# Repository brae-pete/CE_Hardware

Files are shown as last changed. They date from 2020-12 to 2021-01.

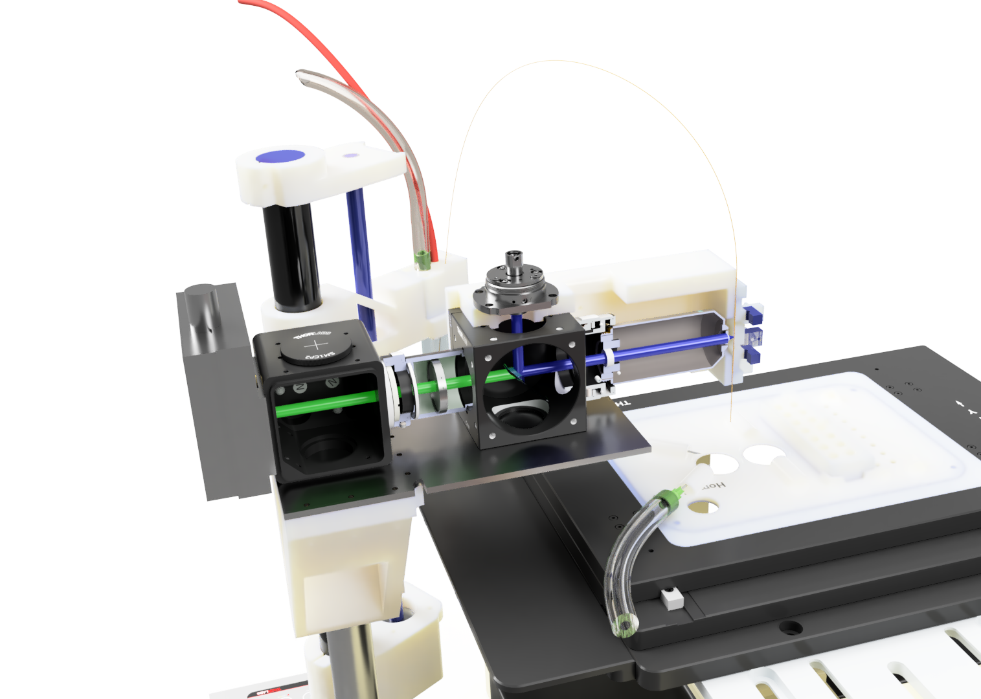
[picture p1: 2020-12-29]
Detection Assembly Light View Optical Components.png

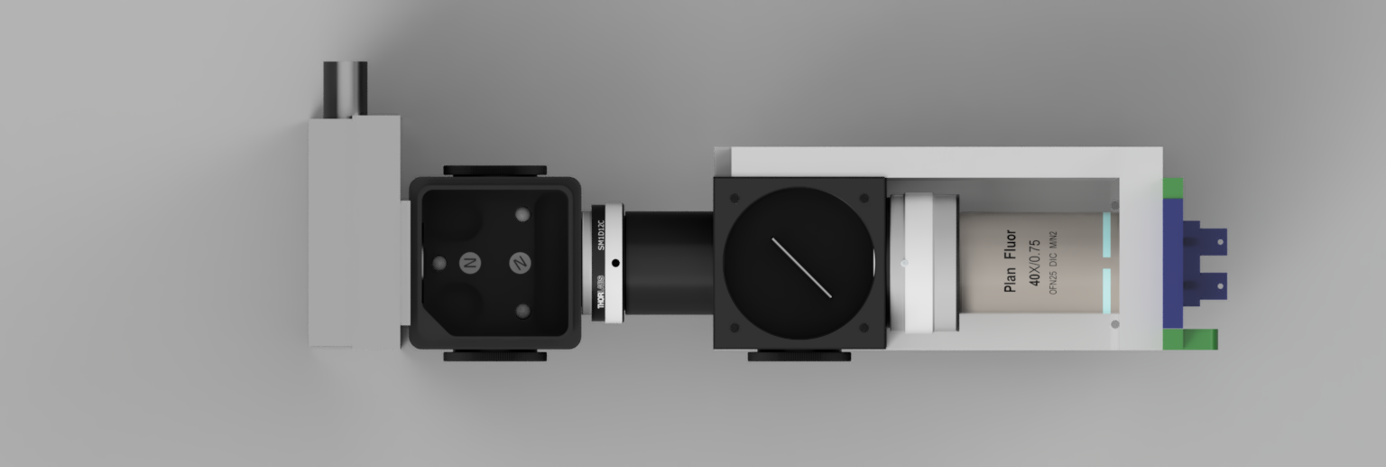
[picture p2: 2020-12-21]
CE Detection Assembly/OpticalAssemblyPurchasedComponents.png

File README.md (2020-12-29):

# CE_Hardware

Repository containing the CAD files and assemblies, as well as diagrams used to build or describe a custom CE instrumentation setup for chemical cytometry. "Assembly Notes" contains an overview of the major components for the CE instrument along with lists of materials, drawings, and diagrams for key assemblies. 

For more in depth coverage see the below articles:

**Building a Chemical cytometry system**

  Abraham, D. H., Anttila, M. M., Gallion, L. A., Petersen, B. V., Proctor, A., & Allbritton, N. L. (2019). Chapter Ten—Design of an automated capillary electrophoresis platform for single-cell analysis. In N. L. Allbritton & M. L. Kovarik (Eds.), Methods in Enzymology (Vol. 628, pp. 191–221). Academic Press. https://doi.org/10.1016/bs.mie.2019.06.016

**Description of the CE Detection assembly and performance**

  Petersen, B. V., Gallion, L., & Allbritton, N. L. (2020). Silicon Photomultipliers as a Low-Cost Fluorescence Detector for Capillary Electrophoresis. Analytical Chemistry, 92(20), 13683–13687. https://doi.org/10.1021/acs.analchem.0c03105

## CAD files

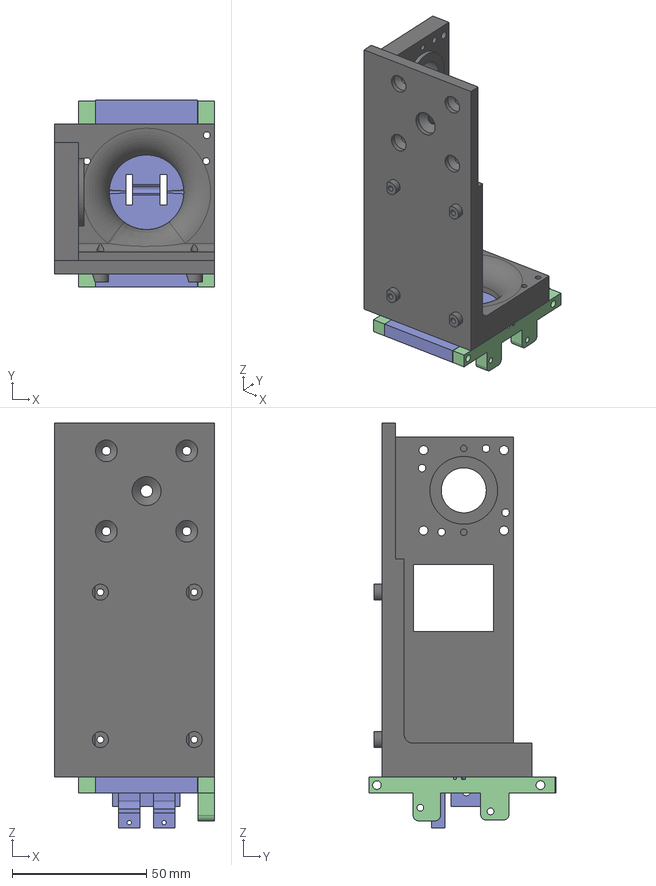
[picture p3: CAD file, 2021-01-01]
CE Detection Assembly/CapillaryAlignmentAssembly.step
59.8 x 69.8 x 151.1 mm
BarracudaCapillaryHolder_Mount v3
CapillaryArm
LowerCapillaryHolderMount
UpperCapillaryHolderMount

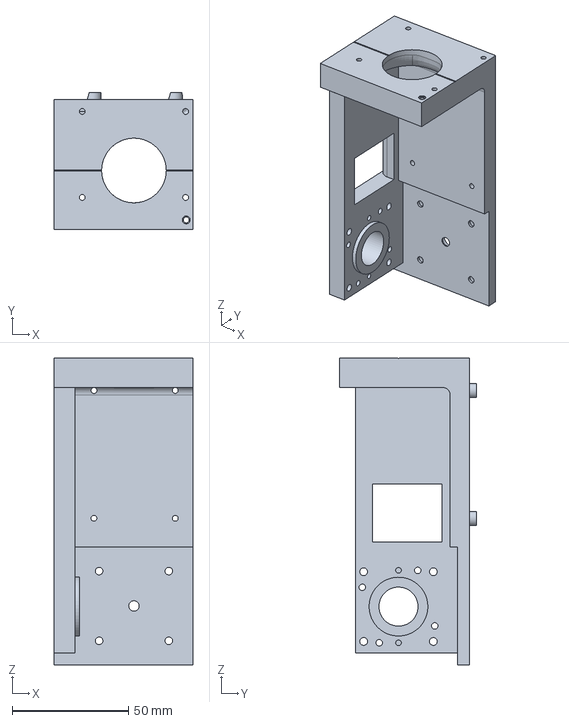
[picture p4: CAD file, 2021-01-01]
CE Detection Assembly/CapillaryArm.step
59.8 x 59.0 x 132.1 mm

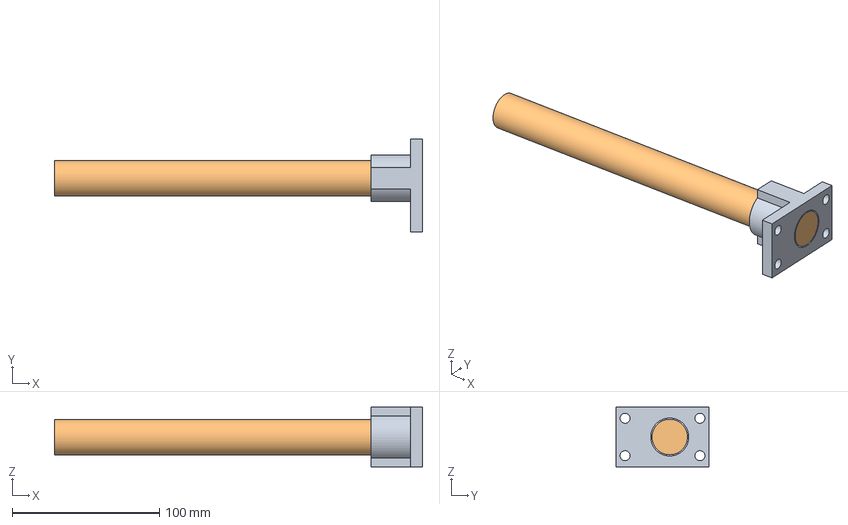
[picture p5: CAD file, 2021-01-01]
CE Detection Assembly/STL/SmoothPostMount.step
250.0 x 63.5 x 40.6 mm

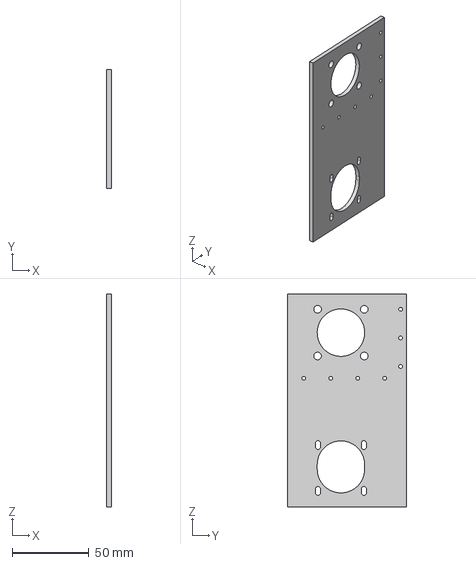
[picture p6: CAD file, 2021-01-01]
CE Detection Assembly/CantileverSupport.step
3.00 x 77.9 x 139.2 mm

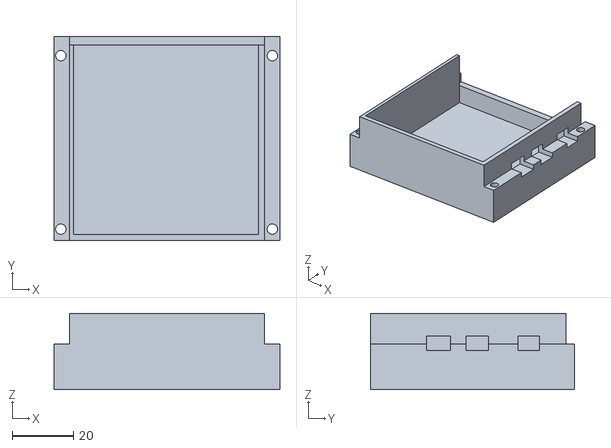
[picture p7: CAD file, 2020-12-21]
CE Detection Assembly/STL/SiPMMount_Upper+Cover.stl
74.0 x 66.8 x 25.0

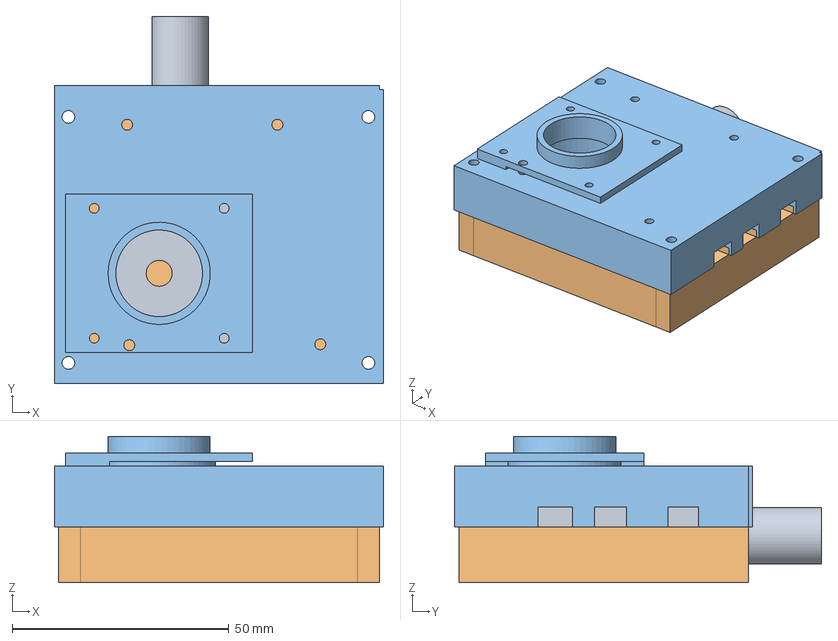
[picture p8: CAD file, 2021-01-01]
CE Detection Assembly/SiPM Mount.step
76.0 x 84.7 x 33.8 mm

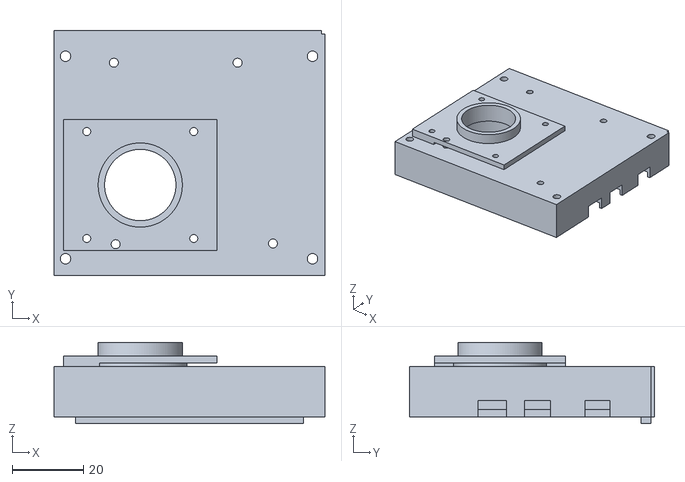
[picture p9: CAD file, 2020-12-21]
CE Detection Assembly/STL/SiPMMount_Bottom_Mount.stl
76.0 x 68.8 x 22.8

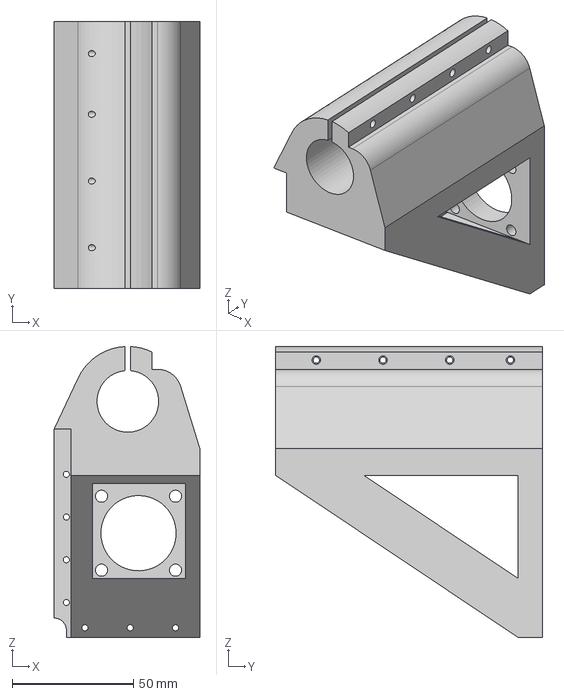
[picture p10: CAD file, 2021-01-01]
CE Detection Assembly/SmoothOpticalSupport.step
60.0 x 110.0 x 119.9 mm

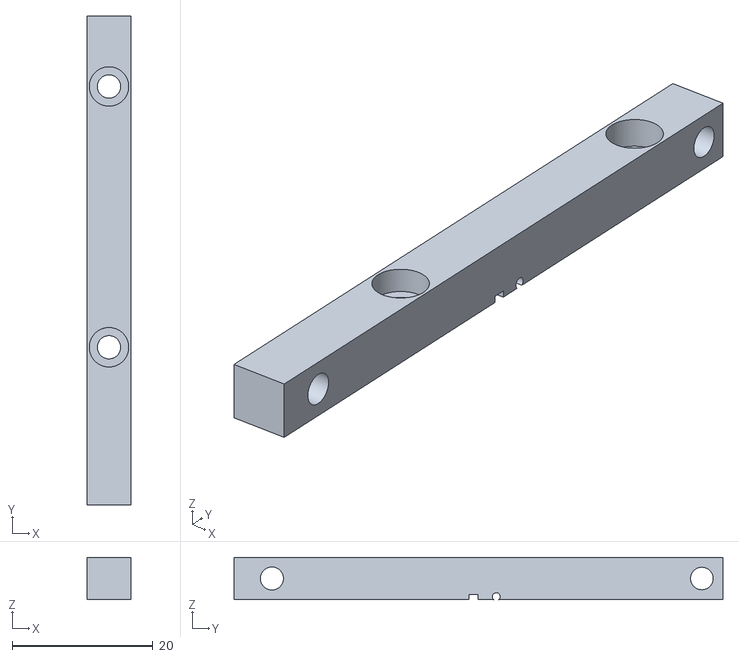
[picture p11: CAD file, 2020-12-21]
CE Detection Assembly/STL/UpperCapillaryHolderMount.stl
6.20 x 69.4 x 6.00

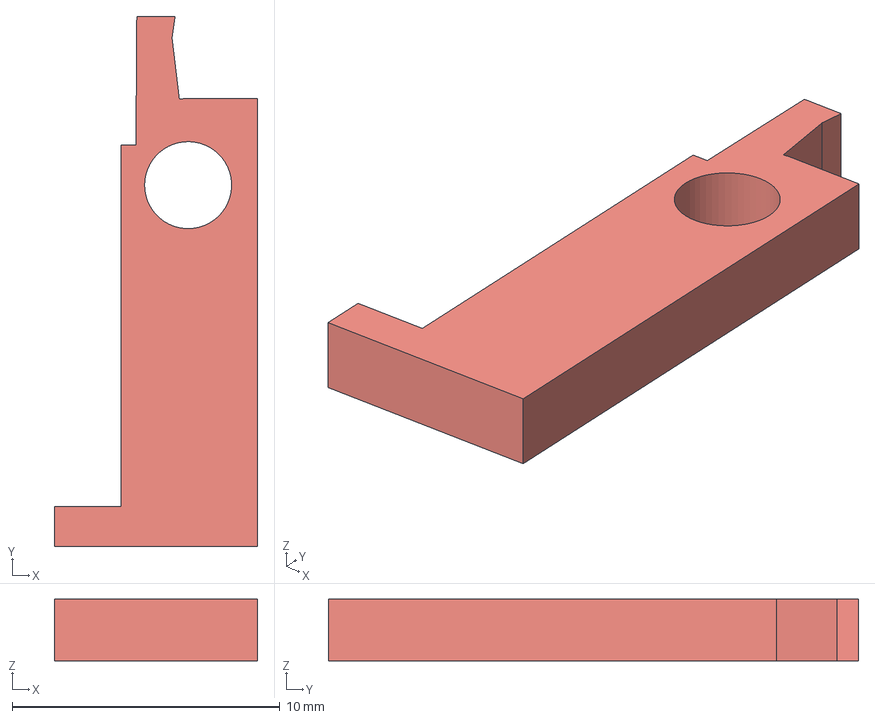
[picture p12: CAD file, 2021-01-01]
CE Detection Assembly/Lever.step
7.60 x 19.8 x 2.30 mm

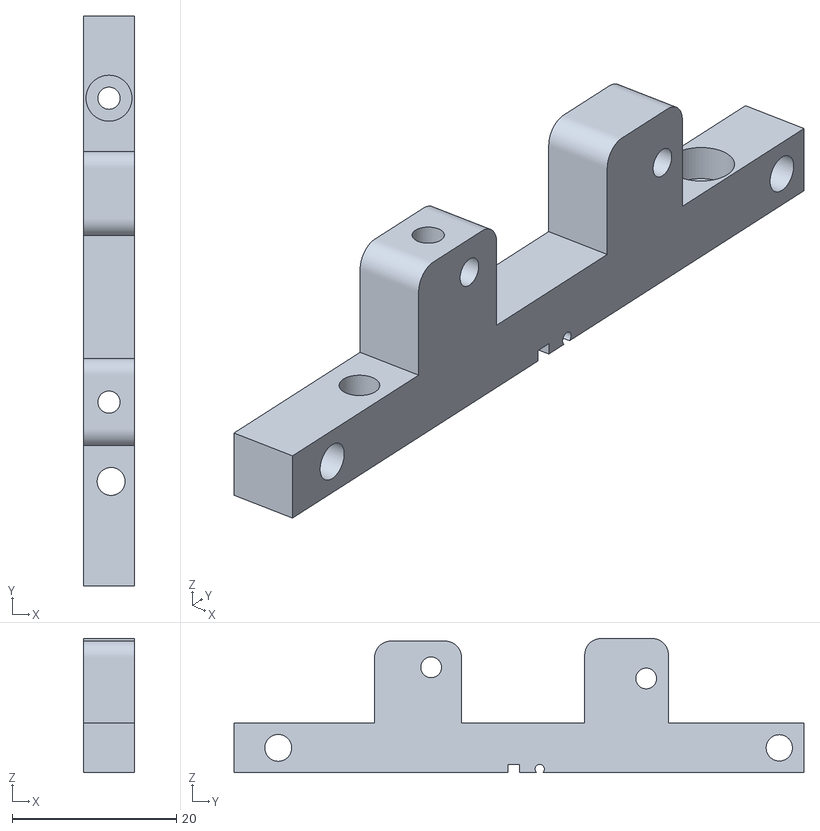
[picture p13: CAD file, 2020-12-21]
CE Detection Assembly/STL/LowerCapillaryHolderMount.stl
6.20 x 69.4 x 16.3

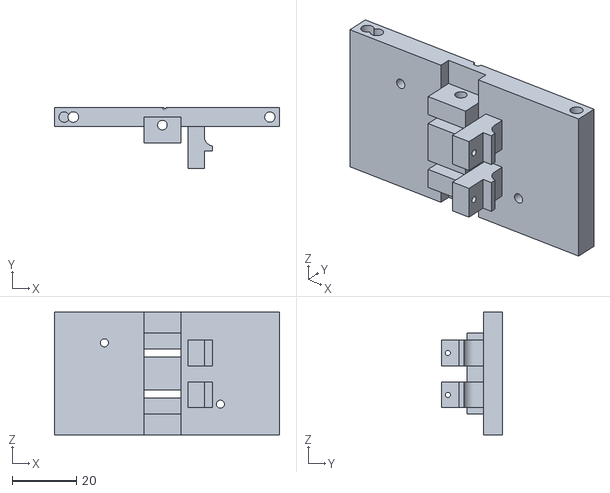
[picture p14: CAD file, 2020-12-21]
CE Detection Assembly/STL/BarracudaCapillaryHolder_Mount v3.stl
69.8 x 19.0 x 38.1

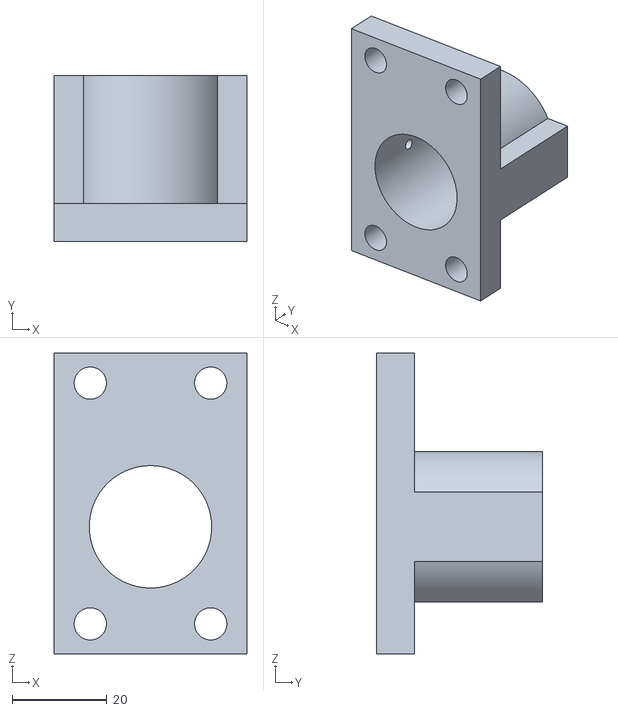
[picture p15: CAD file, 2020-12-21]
CE Detection Assembly/STL/OpticalPostMount v1.stl
40.6 x 35.0 x 63.5

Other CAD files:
CE Detection Assembly/STL/Lever v4.stl
CE Detection Assembly/STL/CantileverSupport.stl
CE Detection Assembly/STL/CapillaryArm.stl
CE Detection Assembly/SmoothPostMount.step
CE Outlet Assembly/Fusion/SmoothRod_Outlet_RemovableEnd v5.f3d

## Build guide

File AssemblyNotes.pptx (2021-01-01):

## Instrument Overview

- Hardware setup can be divided into a few key assemblies:
  - Microscope Assembly
  - CE Detection Assembly
  - CE Outlet Assembly

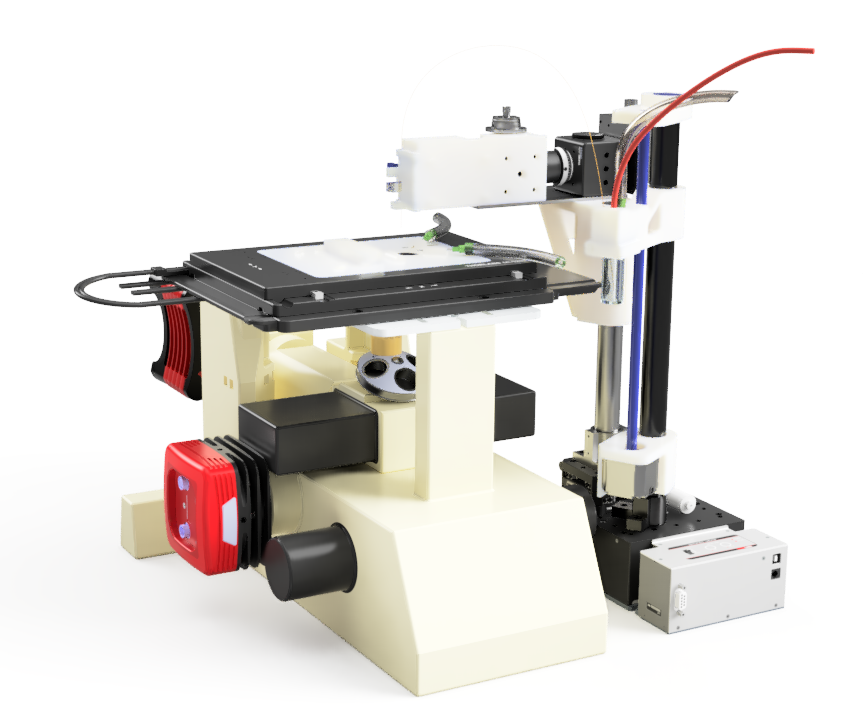
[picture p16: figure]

CE Detection Assembly

CE Outlet Assembly

Microscope Assembly

## CE Detection Assembly Custom Parts

Custom Material List

Object | Material | Fabrication
SiPM Mount | PLA/PETG | 3D Print
Capillary Arm | PLA/PETG | 3D Print
Cantilever Support | Aluminum | Mill
Optical Mount | PLA/PETG | 3D Print
Smooth Post Mount | PLA/PETG | 3D Print
Capillary Alignment Assembly | PLA/PETG | 3D Print
RGB-PCB | FR4 | EDA/PCB Fab.

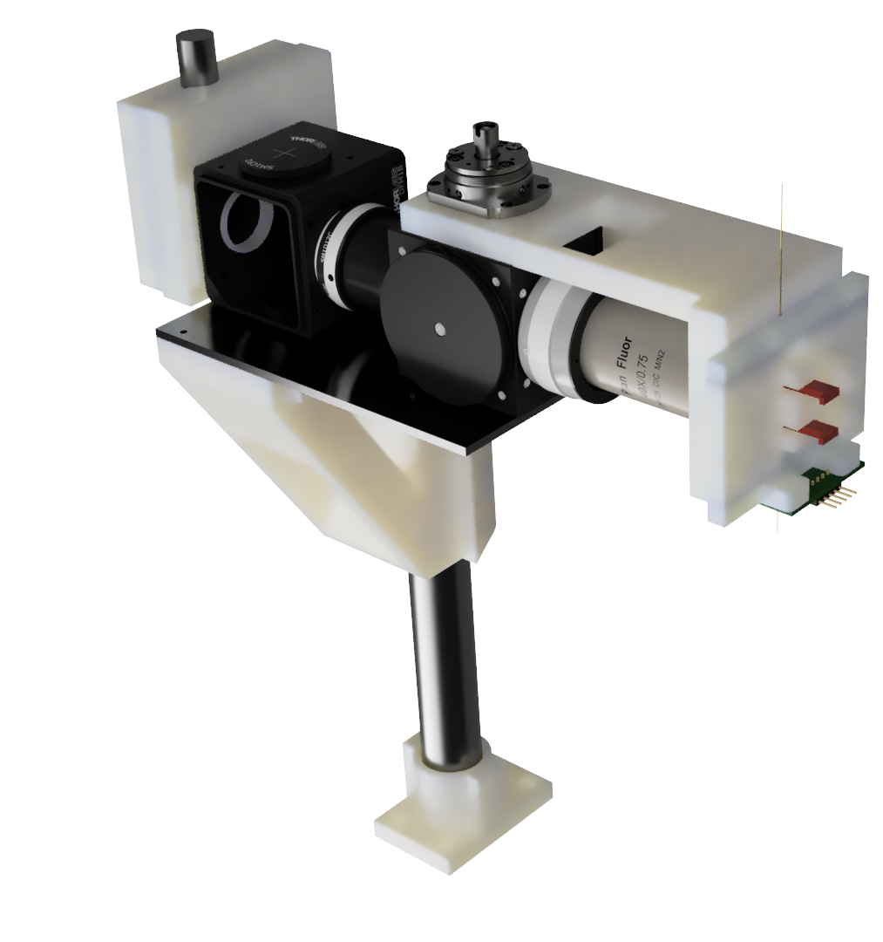
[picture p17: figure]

SiPM Mount

Capillary Arm

Capillary Alignment Assembly

Cantilever Support

Optical Mount

RGB-PCB

Smooth Post Mount

## CE Detection Assembly Purchased Components

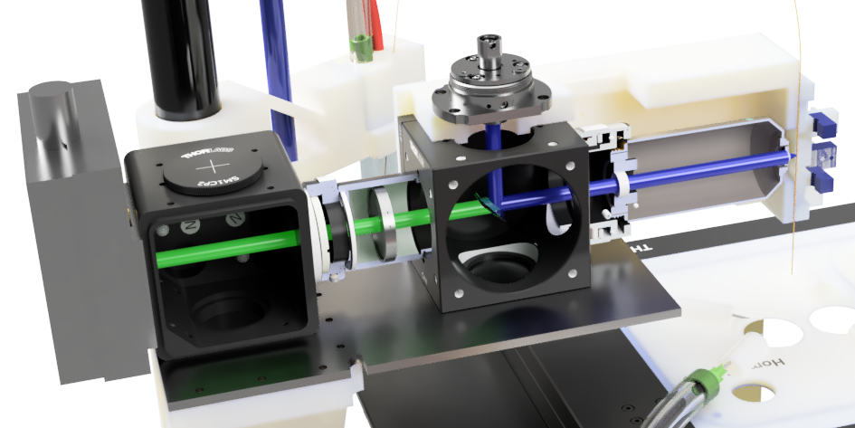
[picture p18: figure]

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
| Component | Company | Part number | Notes
A | 40X Objective 0.75 NA | Nikon
B | 4-Way Mounting Cage | Thorlabs | C4W
C | Cage Dichoic Filter Mount | Thorlabs | FFM1
D | Rotatable Cover Plate | Thorlabs | B3C
E | Blank Cover Plate | Thorlabs | B1C
F | 10 mm Lens Tube | Thorlabs | SM1L10
G | External SM1 threads to internal M25x0.75 Thread (objective) | Thorlabs | SM1A12
H | External C-mount to SM1 thread | Thorlabs | SM1A39 | *PMT
I | Calibrated Iris Diaphragm | Thorlabs | SM1D12C
J | SM1 Threaded Manual Shutter | Thorlabs | SM1SH1 | *PMT
K | End Cap with SM1 Threads | Thorlabs | SM1CP2
L | Non Roating adjustable SM1 Lens Tube | Thorlabs | SM1ZM
M | Dichroic (488 nm) | Chroma | ZT488rdc-UF2 (IN036384) | 25.5 x 36 x 2mm
N | Bandpass Filter (525 +/- 25 nm) | Chroma | ET525/50m (IN005750) | 25 mm dia mounted
O | Notch Filter (488 nm) | Chroma | ZET488NF | 25 mm dia mounted
Q | Fiber Receptacle Collimators | OZ Optics | HPUCO
P | gasket tape | McMaster-Carr | 95705K133 | *PMT .02" thick
R | Optical post | Generic | | 25 mm Diameter

Q

Q

I

N

O

M

Detector

A

Capillary

* Items needed for Hammatsu PMT detector. Can be ignored when using SiPM

## CE Outlet Assembly Custom Parts

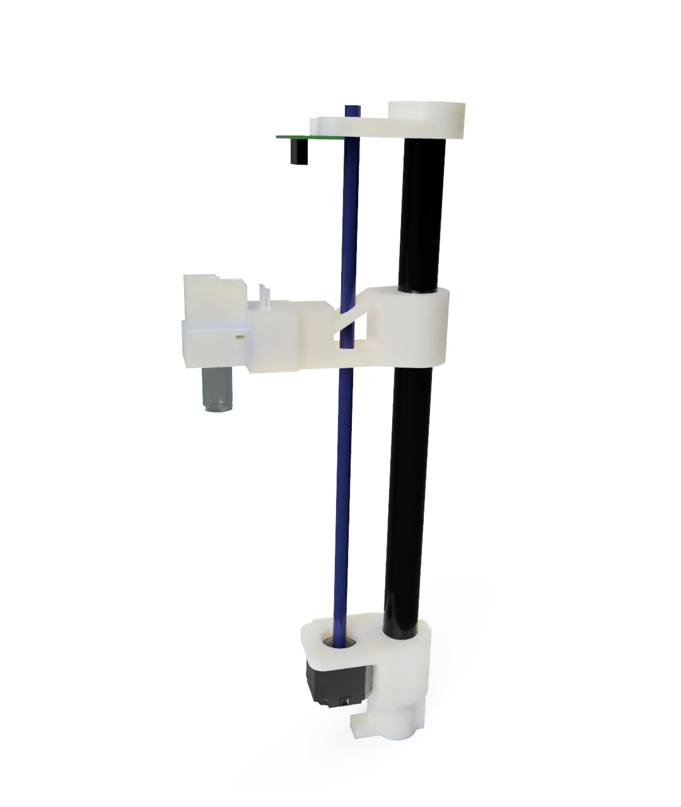
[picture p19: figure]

Lead Screw Smooth Bracket

Limit Switch

Outlet Vial Clamp

Outlet Vial Arm

Motor Smooth Bracket

Optical Post Bracket

Object | Material | Fabrication
Outlet Vial Arm | PLA/PETG | 3D Print
Outlet Vial Clamp | PLA/PETG | 3D Print
Lead Screw Smooth Bracket | PLA/PETG | 3D Print
Motor Smooth Bracket | PLA/PETG | 3D Print
Optical Post Bracket | PLA/PETG | 3D Print
Limit Switch | Breadboard | Snips/Scissors

## CE Outlet Assembly Purchased Components

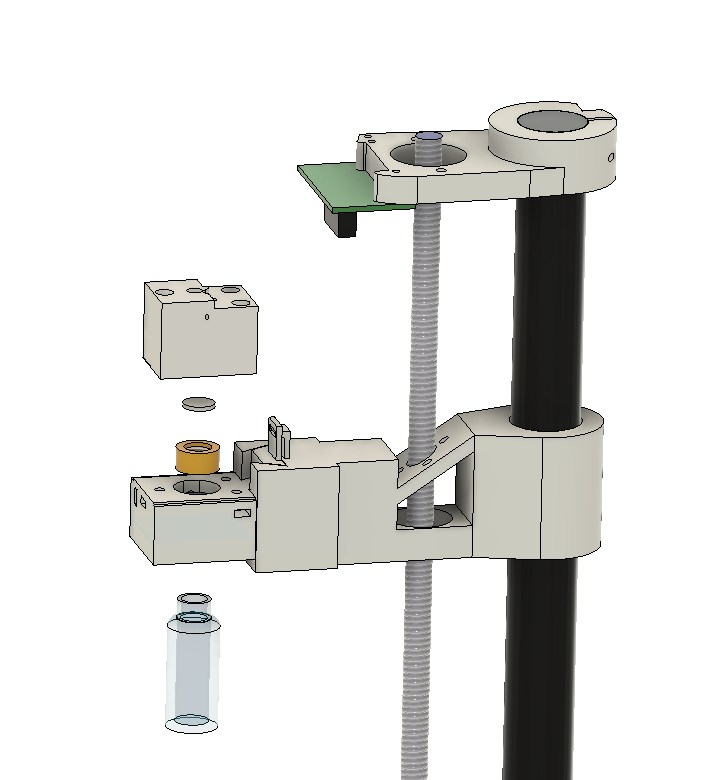
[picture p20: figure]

Breadboard

Limit Switch

Vial cap

Setpum

Vial

LeadScrew

Exploded view of the outlet assembly.

Object | P/N | Supplier | Notes
2.54 mm Pitch Connectors | HDB-635 | Hilitchi, Amazon | Any standard crimped 2.54 mm connectors
Limit Switch | DBWDKG-FT01 | MUZHI, Amazon | Any standard SPDT Switch
Lead Screw w/ Motor and nut | RDX3D060 | Redrex, Amazon | Any leadscrew + motor combo*
Vial, Cap, and Septum | 27340 | MilliporeSigma | Can be swapped with other 4 mL open top screw cap vials with PTFE/Silicon septum.
M3 Nylon Screw | 92492A721 | McMasterCarr | 16 mm L
M3 Screws + Hex Nuts | M3-0420F-SS305 | Iexcell, Amazon | Generic assortment of lengths
Arduino Uno | | Arduino
PowerSTEP01 | X-NUCLEO-IHM03A1 | Mouser
12 V Power Supply | | SmoTecQ, Amazon | The driver can power 12-48V so choose a power supply suitable for your motor.

* 8 mm lead on the lead screw and 1.8° step for the motor will not require adjusting the OutletControl.ino code.

## Limit Switch for Outlet

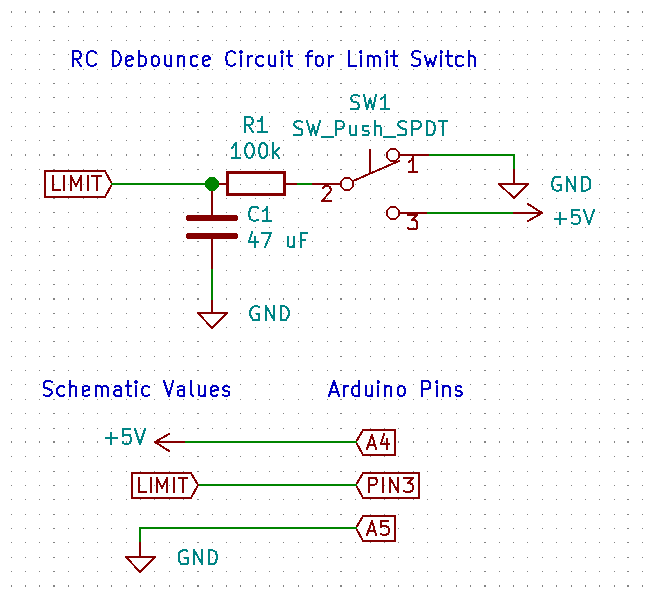
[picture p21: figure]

Wiring diagram for Limit Switch

- Simple through hole bread board can be used.
- Most generic single pull double throw (SPDT) limit switches will work.
- Breadboard can be cut with box cutters or snips. To rough dimensions specified.
- Breadboard will need to have two holes drilled for 3M mounting spaced 35 mm apart, 3.1mm diameter.

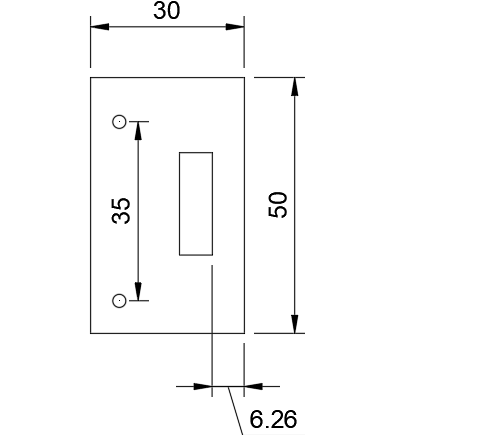
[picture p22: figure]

Breadboard dimensions in mm

## Outlet Arduino Pin Assignments

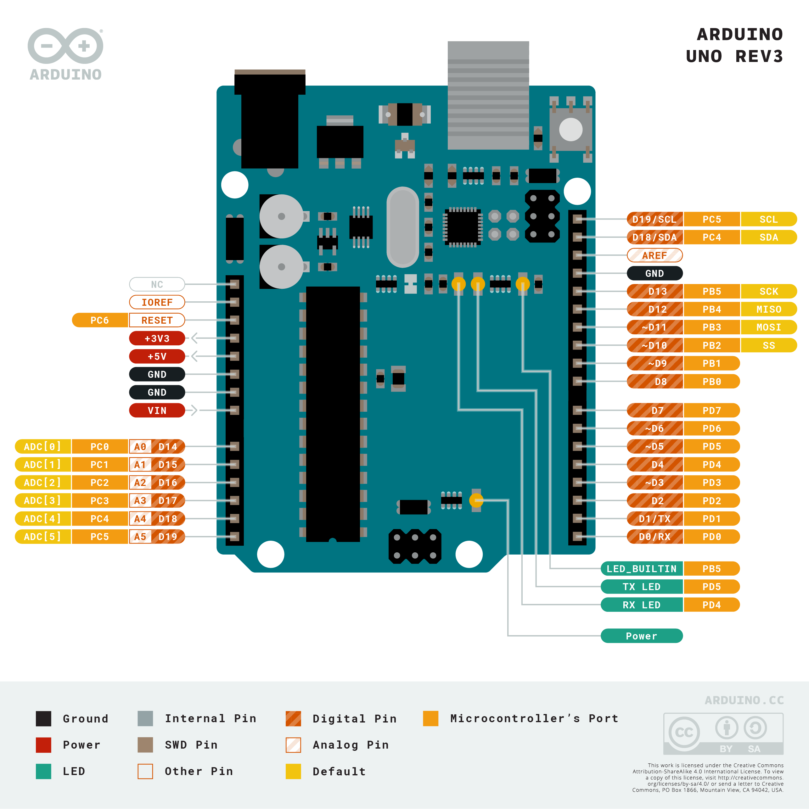
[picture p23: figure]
Arduino Uno Rev3 | Arduino Official Store

Solenoid

SOLENOID

LIMIT

RGB LED

LIMIT

https://store.arduino.cc/usa/arduino-uno-rev3

- Place the X-Nucleo ontop of the Arduino Uno.
  - Pin spacing is the same for Nucleo and Arduino Uno.
- 3 Wires are reserved for the limit switch (A4, A5, D3).
- 3 Wires are reserved for the inlet RGB LED (A1, A2, A3)
- 3 Wires are reserved for the Solenoid (D4, D6, & D7)
- Wire the stepper motor to the Nucleo output screw terminals (A+/A-, B+/B-).
  - Each coil of the stepper motor is indicated by A or B. Identify which leads correspond to the same coil using an Ohm meter.
- Connect the 12 V power supply to the Nucleo power screw terminals (Labeled GND and +V).

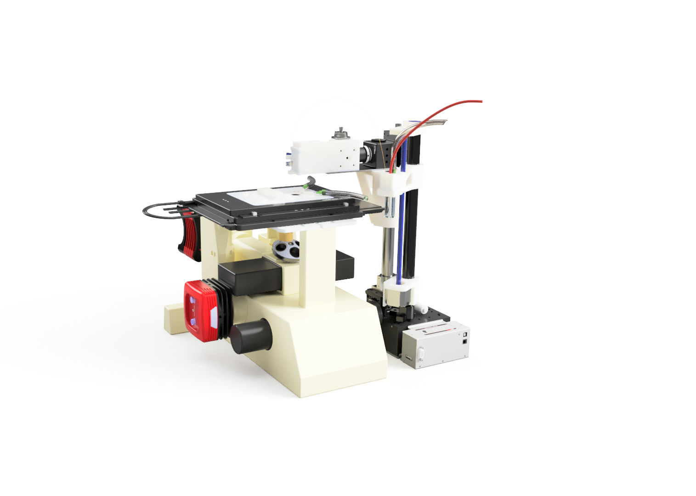
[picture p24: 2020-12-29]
AssemblyOverview.PNG

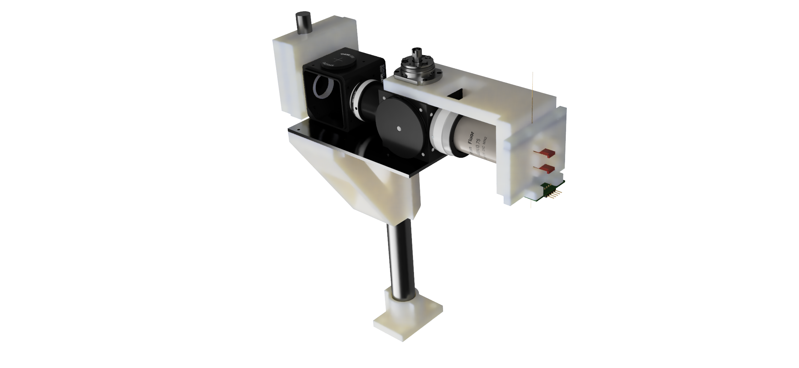
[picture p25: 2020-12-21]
CE Detection Assembly/OpticalAssemblyView.png

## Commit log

2020-12-21 Optical Assembly Upload
    Optical Assembly Parts, STEP, and STL files with BOM in Assembly Notes
    [CantileverSupport.step, CapillaryAlignmentAssembly.step, CapillaryArm.step]
2020-12-21 Optical Assembly
    [BarracudaCapillaryHolder_Mount v3.stl, CantileverSupport.stl, CapillaryArm.stl, Lever v4.stl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]
2021-01-01 Folder Rename. Assembly notes updating.
    [BarracudaCapillaryHolder_Mount v3.stl, CantileverSupport.step, CantileverSupport.stl, CapillaryAlignmentAssembly.step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]
